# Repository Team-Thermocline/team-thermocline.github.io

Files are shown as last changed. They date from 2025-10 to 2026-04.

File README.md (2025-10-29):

# thermocline.github.io

SNHU 2025-2026 capstone project.
Team Thermocline.

# Building this website

To run this project locally using Vite, follow these steps:

Clone this repo.
```shell
git clone https://github.com/Team-Thermocline/thermocline.github.io.git
cd thermocline.github.io
```

Install deps
```shell
npm install
```

Run the dev server
```shell
npm run dev
```

# Tools

Make a new update
```shell
npm run new-update
```

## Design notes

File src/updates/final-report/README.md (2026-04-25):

---
date: 2026-04-25
---

# Final Report

Our final report

Abstract:
SNHU’s final capstone course required students to collaborate across engineering disciplines to
design, fabricate, test, analyze, optimize, and present a working product that satisfied customer
requirements. Each student brought their unique mechanical and electrical experience to help
develop the final product: a thermally-controlled PCB testing chamber that delivered efficient and
highly successful performance. Team Thermocline was originally presented with several driving
requirements provided by the customer – an electrical engineering professor, which described
product dimension, function, and performance criteria. From this, the group developed a
conceptual design, including materials, components, control features, and the expected assembly
integration process. Trade studies were then conducted across the project, supported by external
consultations with engineering, HVAC, and manufacturing/machining professionals to approve – or
improve – the product design. Initial studies included prototype electronic boards and mechanical
parts to test supply chain capabilities and electronic performance feasibility. The team built on
these initial steps by designing the mechanical structure, creating the main electronic control
board, sourcing thermal-fluid components, ordering critical pieces, and 3D-printing/laser-cutting
parts. Assembly was supplemented with iterative designing, prototyping, and functional testing of
individual subsystems. The end of the course brought performance testing to observe alignment
with customer requirements, and presenting to relevant project stakeholders. Proper
documentation was completed throughout the project, showing clear product development
history. By the end, all system and driving customer requirements were met, achieved by
persistent, insightful, and collaborative teamwork. However, one derived requirement was not met
(CON-05), describing the prohibition of thermal control when the user is handling the PCB. This
resulted from a lack of testing with physical PCBs inside the chamber, and implementing the
necessary sensors/measurements/controls to enforce this requirement. In spite of this, the team
successfully designed, built, and tested the thermally-controlled chamber that met/exceeded
most requirements, and served as an enlightening experience for developing well-rounded
engineers.

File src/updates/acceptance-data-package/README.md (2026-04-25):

---
date: 2026-04-23
---

# Acceptance Data Package

The Acceptance Data Package contains all CAD, writeup, design and software/firmware
resources for the entire project.

Its a lot to download!

|               File Name                |  Type   |                                        Description                                         |
| -------------------------------------- | ------- | ------------------------------------------------------------------------------------------ |
| ADP Summary Index                      | .docx   | *This document                                                                             |
| Bundle-3d-printing-kit                 | .zip    | All .stl/.stp files used for 3D printing prototypes and final parts                        |
| Bundle-gasket-kit                      | .zip    | CAD files for gaskets/seals                                                                |
| Bundle-scs-order-1                     | .zip    | CAD files used in purchasing SendCutSend panels (order #1)                                 |
| Bundle-scs-order-2                     | .zip    | CAD files used in purchasing SendCutSend panels (order #2)                                 |
| Bundle-scs-order-3                     | .zip    | CAD files used in purchasing SendCutSend panels (order #3)                                 |
| Bundle-scs-order-4                     | .zip    | CAD files used in purchasing SendCutSend panels (order #4)                                 |
| Controller Board BOM (LCSC)            | .xl     | Controller board materials/parts                                                           |
| Controller Board Gerbers               | .zip    | Controller board design files                                                              |
| Controller Manual                      | .pdf    | Instruction manual for product specifications, installation, and troubleshooting           |
| Developmental Steps                    | .zip    | Design plan documents and test results related to the technical development of the product |
| Team Thermocline Poster                | .pdf    | Final poster used in the open-house presentation                                           |
| thermocline_controller_v1.1-1-g5ebd8be | .uf2    | Controller firmware                                                                        |
| Thermocline Logos.zip                  | .zip    | Vector graphics, PNG graphics and original logo/style design components                    |
| ThermoclineHMI_V0.2.tar.gz             | .tar.gz | Tarball of the HMI firmware                                                                |

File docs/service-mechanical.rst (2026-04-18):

******************
Mechanical Service
******************

Regular Maintenance
===================

Serivce schedule is based on our best guess, we have not tested the machine for months at a time and certainly not a year.
Feel free to edit this page and adjust to the schedule that presents itself.

+----------------------------+-----+------+-------+-------+--------+--------+------------+
|                            | 1hr | 6hrs | 10hrs | 50hrs | 100hrs | 500hrs |  1000hrs   |
+============================+=====+======+=======+=======+========+========+============+
| Chamber gasket             |     |      |       | x     | x      | x      | x          |
+----------------------------+-----+------+-------+-------+--------+--------+------------+
| Check door gasket          |     |      |       |       | x      | x      | x          |
+----------------------------+-----+------+-------+-------+--------+--------+------------+
| Refrigerant System         |     |      |       |       |        |        | Run yearly |
+----------------------------+-----+------+-------+-------+--------+--------+------------+
| Check Internal Fan         |     |      |       | x     |        |        |            |
+----------------------------+-----+------+-------+-------+--------+--------+------------+
| Chamber Level              |     |      |       |       | x      |        |            |
+----------------------------+-----+------+-------+-------+--------+--------+------------+
| Check condenser attachment |     |      |       |       | x      |        |            |
+----------------------------+-----+------+-------+-------+--------+--------+------------+
| 3D Prints                  |     |      | x     |       |        |        |            |
+----------------------------+-----+------+-------+-------+--------+--------+------------+

See runtime hours in the **Debug Values** section of the HMI touch screen (:ref:`hmi-debug-values`).

System Structure
================

Inside the insulation houses the main chamber core. The basic assembly looks like this:

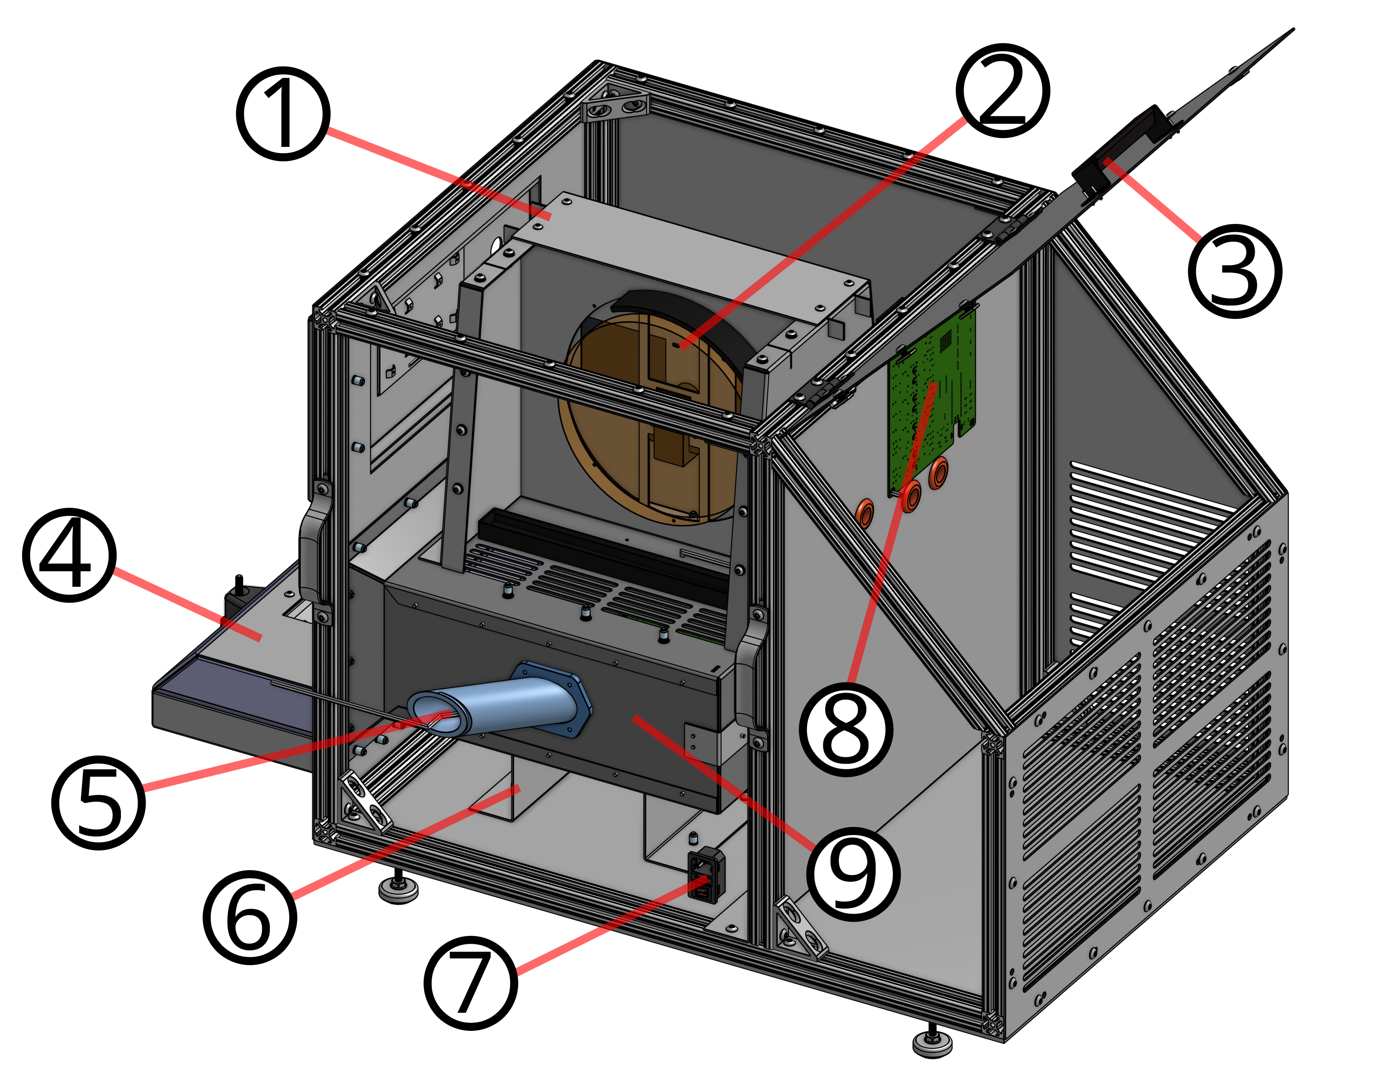
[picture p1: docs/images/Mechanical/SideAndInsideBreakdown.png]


+--------+----------------------------+
| Number |        Description         |
+========+============================+
| 1      | "Trapezoid" outer paneling |
+--------+----------------------------+
| 2      | Circulation Fan            |
+--------+----------------------------+
| 3      | Machinery Access Door      |
+--------+----------------------------+
| 4      | Chamber Door               |
+--------+----------------------------+
| 5      | Wire Passthrough Port      |
+--------+----------------------------+
| 6      | Chamber Pedestal           |
+--------+----------------------------+
| 7      | IEC Receptacle             |
+--------+----------------------------+
| 8      | Chamber Controller Board   |
+--------+----------------------------+
| 9      | Chamber Shroud             |
+--------+----------------------------+

Installing and Uninstalling panels
==================================

The chamber is built with many laser cut panels. These panels are held to an internal aluminum
extrusion frame with 1/4-20 screws and nuts, as well as 10-32 screws and rivnuts in some places.

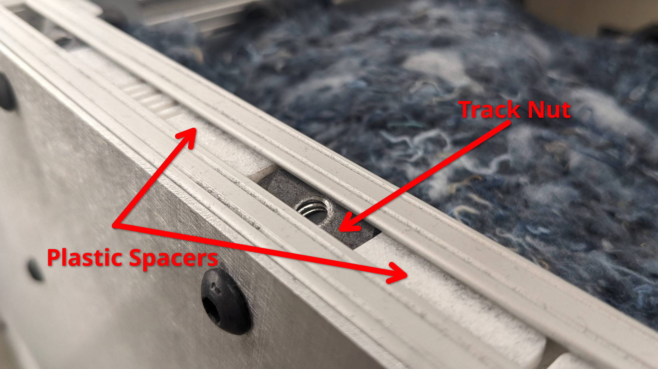
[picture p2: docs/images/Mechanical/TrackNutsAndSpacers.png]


.. note:: When installing screws, the track nuts can often become missaligned. Leave all screws loose until each screw is started, then tighten down. This allows some flexibility to correct missalignment.

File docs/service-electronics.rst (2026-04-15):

******************
Electrical Service
******************

Main Board
==========

The Main Board is the central controller PCB for the thermal testing chamber. It handles all the critical measuremnts, the high-power switching
and the centeral interconnect between HMI, a user laptop and the physical hardware.

Schematics
==========

The schematic files are stored on our 
`GitHub repository <https://github.com/Team-Thermocline/Controller/tree/main/Hardware/Main-Board>`_, 
but can also be viewed via `KiCanvas <https://kicanvas.org/>`_ 
on the web or at the end of the printed PDF Manual.

+-------------+---------------------------------------------------------------------------------------------------------------------------------------------------------------------------------------------------------------+
| Full System | `Full System Schematic <https://kicanvas.org/?repo=https%3A%2F%2Fgithub.com%2FTeam-Thermocline%2FController%2Fblob%2Ffeat%2Ffull_system_schematic%2FHardware%2FComplete-System%2FComplete-System.kicad_sch>`_ |
+=============+===============================================================================================================================================================================================================+
| Mainboard   | `Mainboard Interactive Schematic <https://team-thermocline.github.io/schematics/Main-Board.html#/>`_                                                                                                          |
+-------------+---------------------------------------------------------------------------------------------------------------------------------------------------------------------------------------------------------------+

Fuses
=====

The chamber uses 6 fuses total. One on the IEC plug on the side. And five more on the main board under
the rear panel.

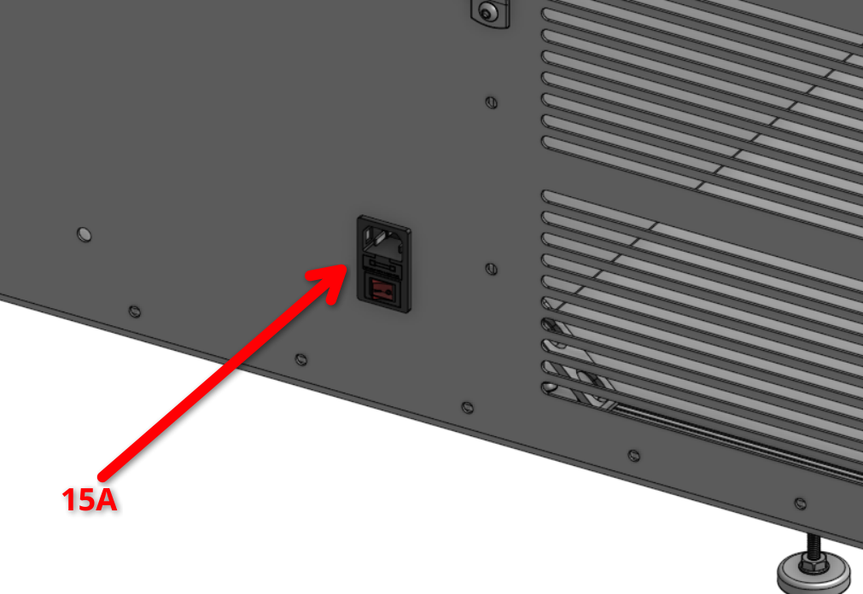
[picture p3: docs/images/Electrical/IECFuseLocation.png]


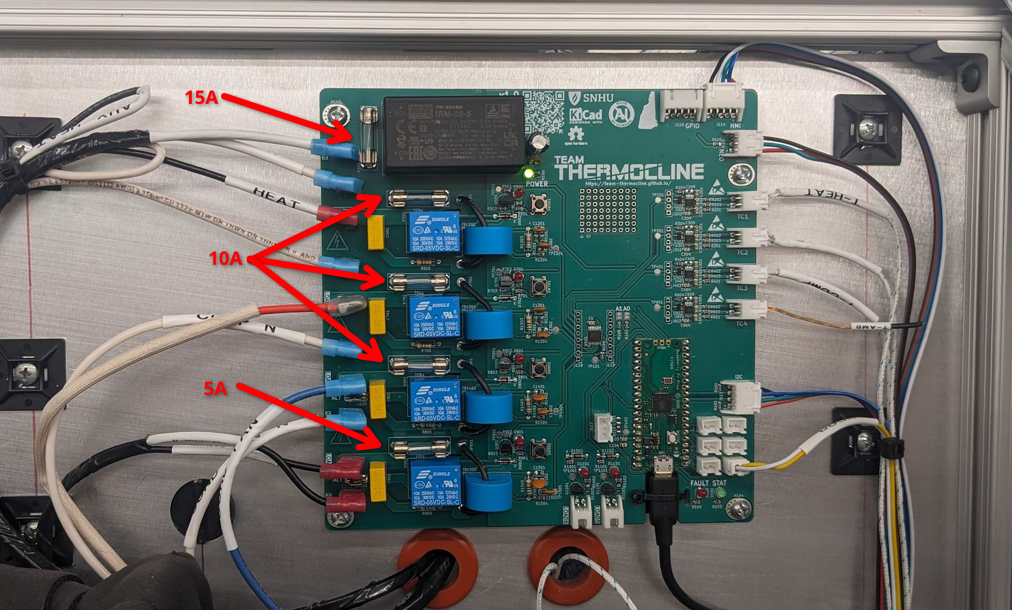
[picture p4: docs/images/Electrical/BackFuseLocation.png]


There are three main fuses sizes, 15A, 10A and 5A.

.. warning:: Power the system down and unplug it before changing fuses! Fuses are LIVE when powered on!

Decorational Panel
==================

The decorational panel is a large sheet metal panel at the front of the machine that houses the raspberry
pi 5 HMI as well as the machine USB-C port and the E-Stop button.

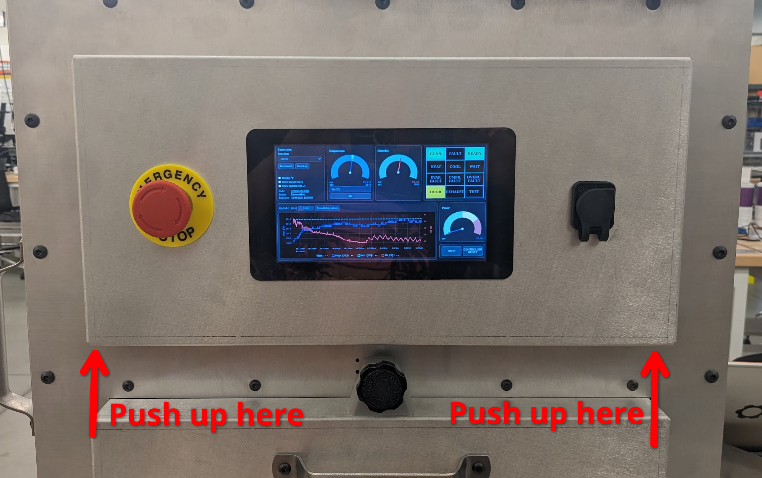
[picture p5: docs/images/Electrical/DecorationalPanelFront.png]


The panel can be removed by pushing up evenly from the bottom and pulling gently off the front. It is
held in place by four screws in locking slots.

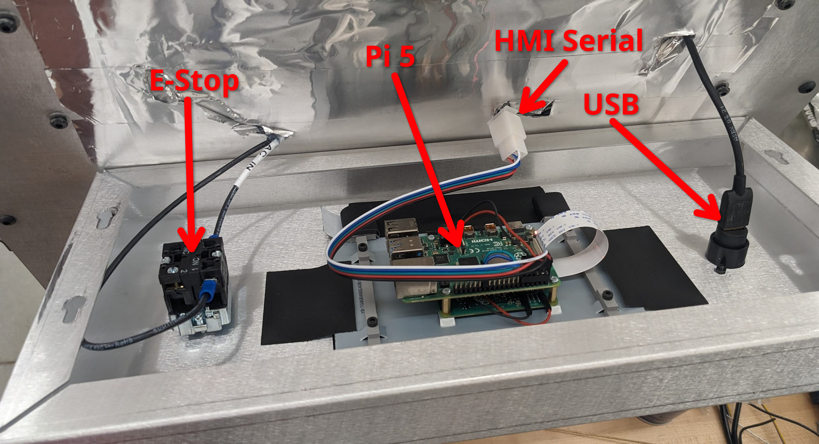
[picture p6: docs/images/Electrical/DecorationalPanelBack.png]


PCB Files
=========

* `Click here to View Layout <https://kicanvas.org/?repo=https://github.com/Team-Thermocline/Controller/blob/v1.0/Hardware/Main-Board/Main-Board.kicad_pcb>`_
  (PCB rendered and hosted on KiCanvas! There may be visual bugs; for best browsing experience view the PCB directly in KiCad!)

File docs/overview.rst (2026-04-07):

Project Overview
================

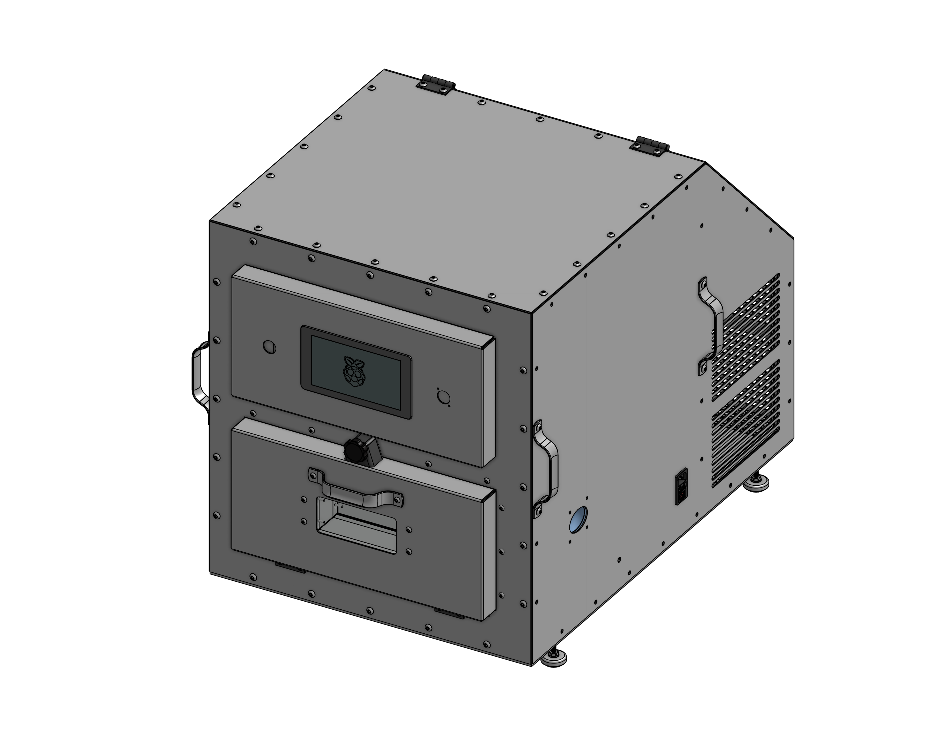
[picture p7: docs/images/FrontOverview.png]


The Team Thermocline Thermal Testing Chamber (Refered to as "The Chamber") is a thermal testing chamber designed to test the 
performance of electronic components in a controlled environment. It was designed as a 2025-2026 engineering capstone project 
at Southern New Hampshire University (SNHU).

The Chamber is 22" by 31" and weighs about 90lb. When lifting the chamber, please use at least a *two person lift*.

Powering the Chamber on
-----------------------

The chamber is powered by an IEC cable connected to a recepticale on the right side of the machine (when facing the front).
Please note the chamber is fused for 15A.

There are two AC interlocks, one is the red switch on the side controlling the system power, the other is the E-Stop button on
the front. Both must be in the "on" position for the chamber to power on. Twist the E-Stop button to reset it back to on.

The chamber uses both a raspberry pi pico as the primary controller and a raspberry pi 5 as a build-in screen. The pico
should boot almost imedietly after power is applied, and should turn on the chamber lights.
*The pi 5 may take one or two minutes to boot.*

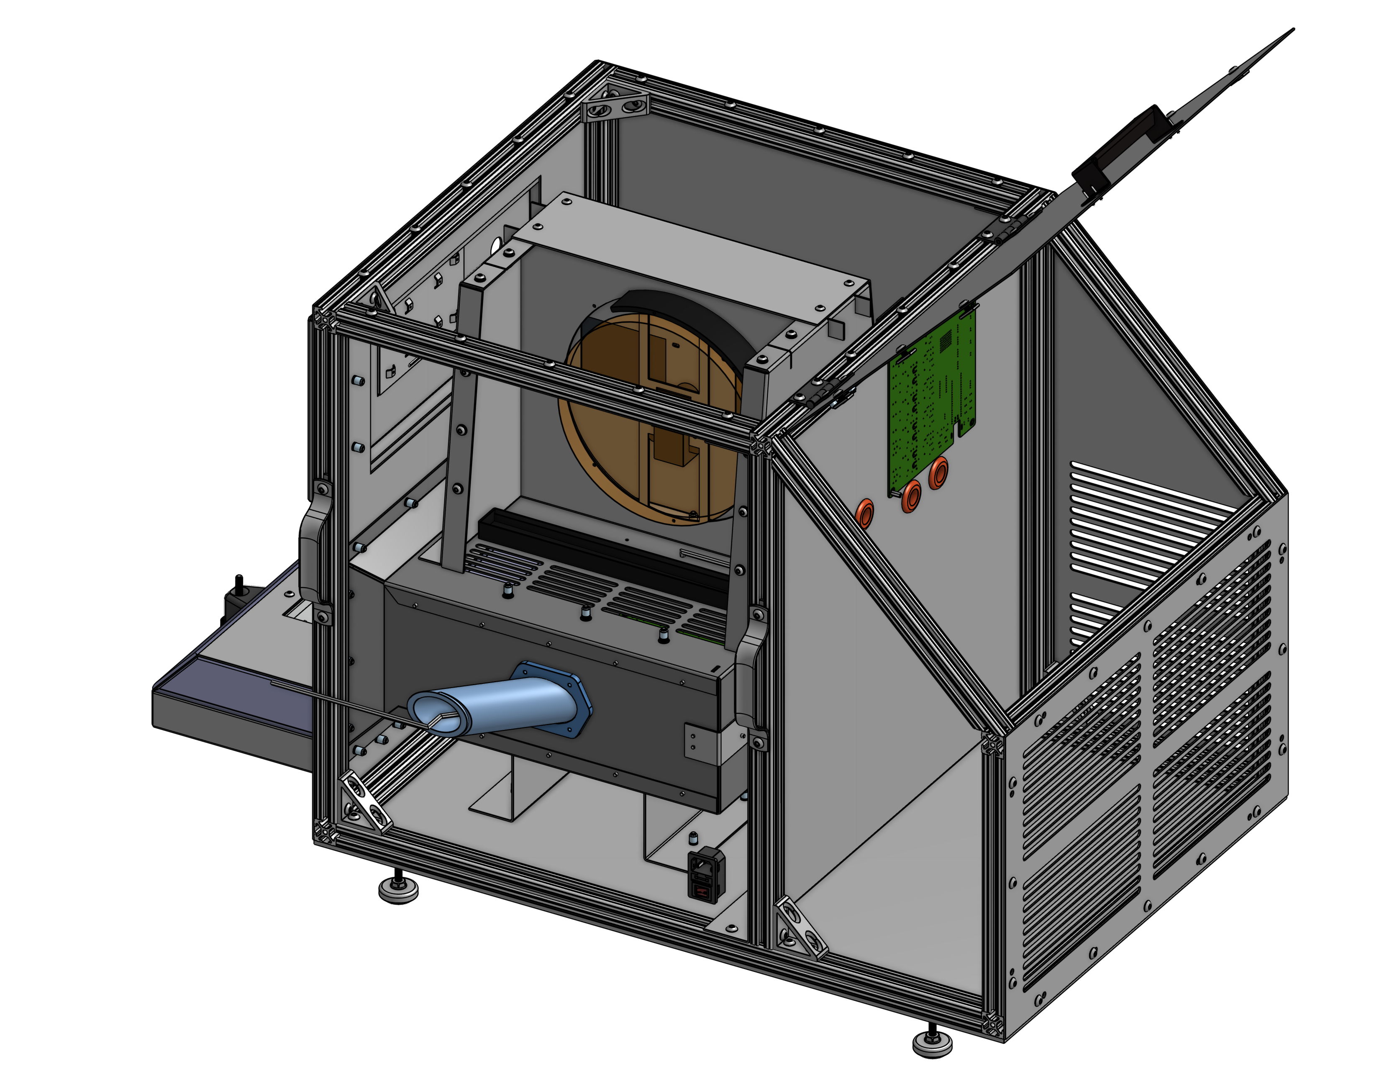
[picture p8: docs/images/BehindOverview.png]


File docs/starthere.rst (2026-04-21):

**********
Start Here
**********

The Team Thermocline Thermal Testing Chamber (Refered to as "The Chamber") is a thermal testing chamber designed to test the 
performance of electronic components in a controlled environment. It was designed as a 2025-2026 engineering capstone project 
at Southern New Hampshire University (SNHU).

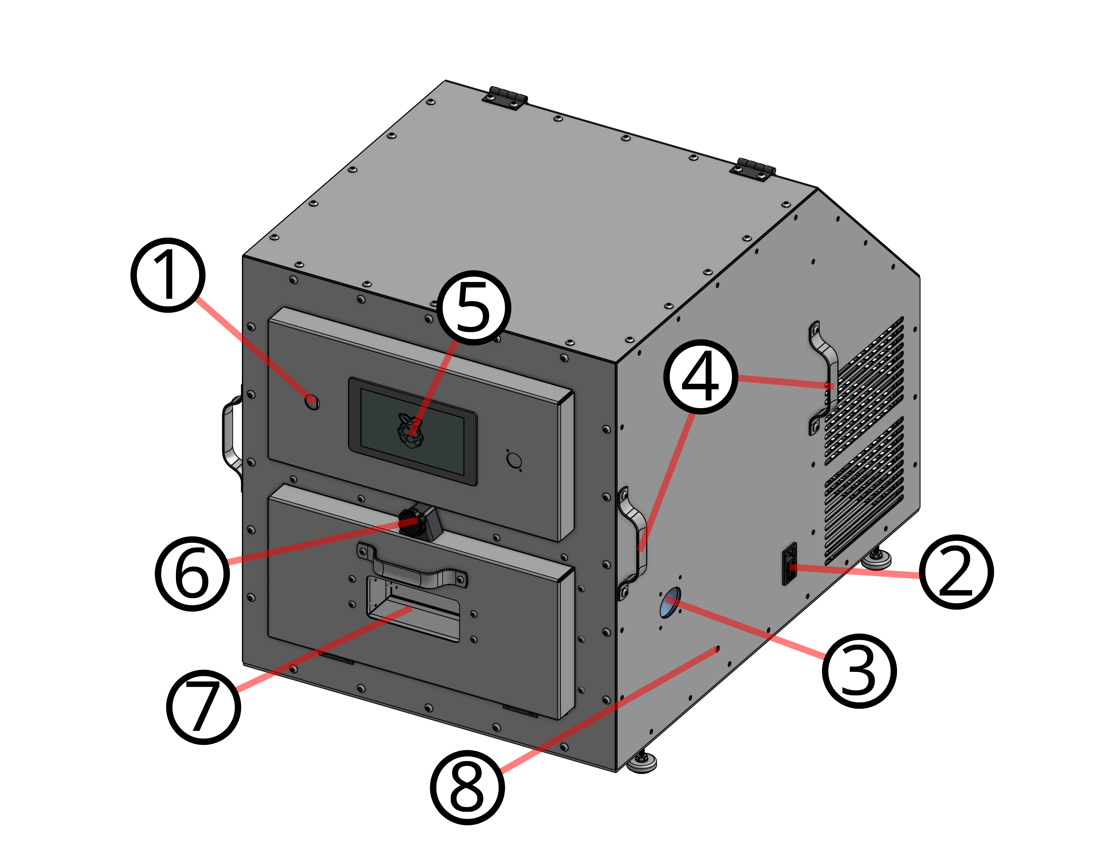
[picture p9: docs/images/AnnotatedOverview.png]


+--------+-----------------------+
| Number |      Description      |
+========+=======================+
| 1      | E-Stop Button         |
+--------+-----------------------+
| 2      | IEC Receptacle        |
+--------+-----------------------+
| 3      | Wire Passthrough Port |
+--------+-----------------------+
| 4      | Lifting Handles       |
+--------+-----------------------+
| 5      | HMI Touch Screen      |
+--------+-----------------------+
| 6      | Door Locking Clamp    |
+--------+-----------------------+
| 7      | Viewing Window        |
+--------+-----------------------+
| 8      | Condensate Drain Port |
+--------+-----------------------+

This manual references things in terms of **Left** and **Right** side of the machine.

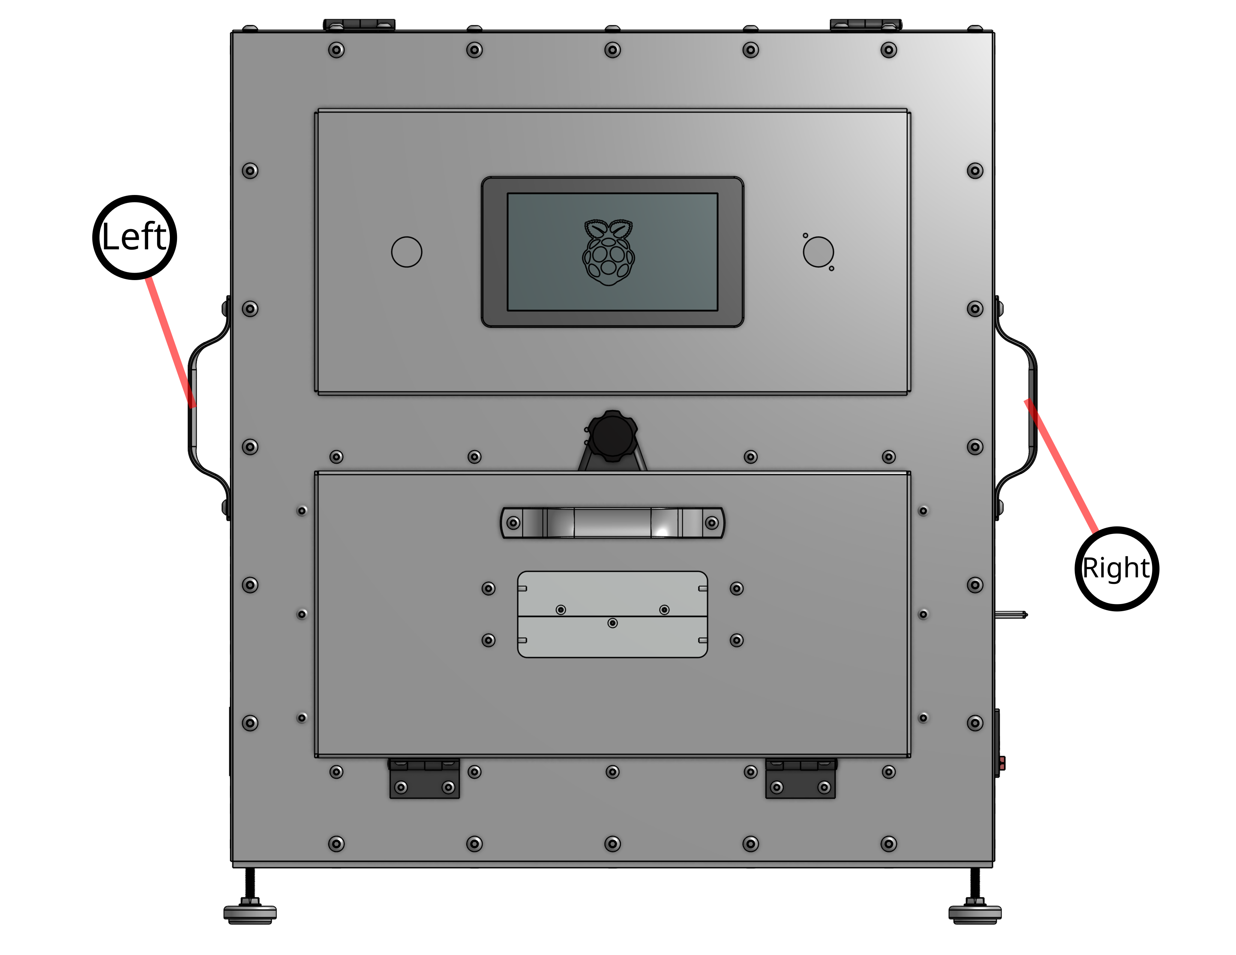
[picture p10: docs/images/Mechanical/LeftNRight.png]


Moving the Chamber
==================

.. warning:: The Chamber is 22" by 31" and weighs about 125lb. When lifting the chamber, please use at least a *two person lift*.

The chamber has handles located on either side. With two or four people, lift each handle vertically 
to move the chamber. Do not rotate the chamber as this may cause fluids to move into unintended parts
of the plumbing. Do not shake or jostle the chamber as hard shocks can damage plumbing.

.. note:: Because the cooling system of the chamber can collect water, the chamber should be leveled
    along its long axis to allow for proper drainage.

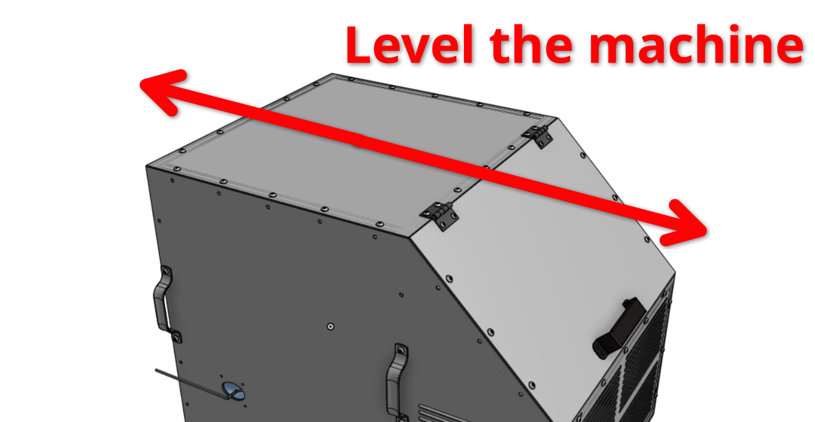
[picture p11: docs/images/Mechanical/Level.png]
    

Place the chamber in such a way that there is enough area to vent air directly out the back.
Allow for no less than **8"** of clearance behind the chamber.

Powering the Chamber on
=======================

The chamber is powered by an IEC cable connected to a recepticale on the right side of the machine (when facing the front).

There are two AC interlocks, one is the red switch on the side within the IEC receptacle(2), the other is the E-Stop button on
the front(1). Both must be in the "on" position for the chamber to power on. Twist the E-Stop button to reset it back to on.

The chamber uses both a raspberry pi pico as the primary controller and a raspberry pi 5(5) as a build-in screen. The pico
should boot almost imedietly after power is applied, and should turn on the chamber lights.
**The pi 5 may take one or two minutes to boot.**

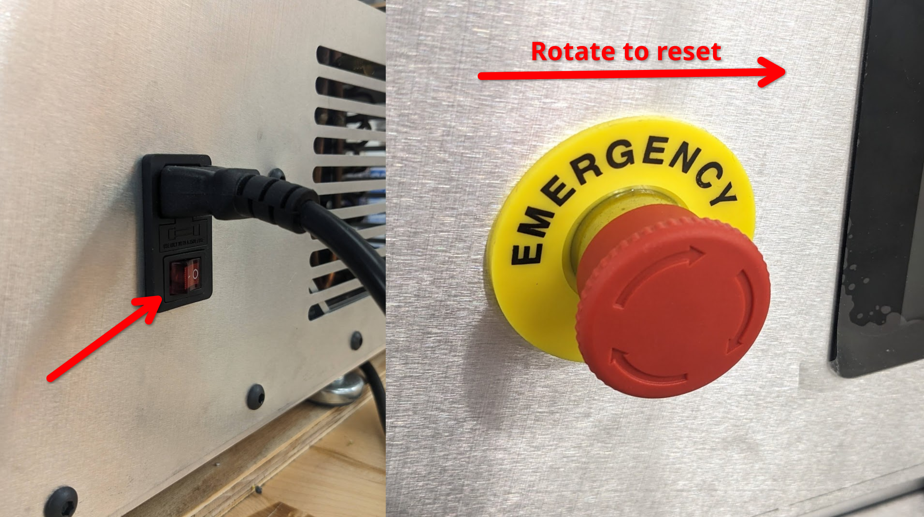
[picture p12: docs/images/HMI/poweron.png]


Using the HMI Touch Screen
==========================

Once the HMI is booted (which can take one to two minutes), you should see the main HMI screen.

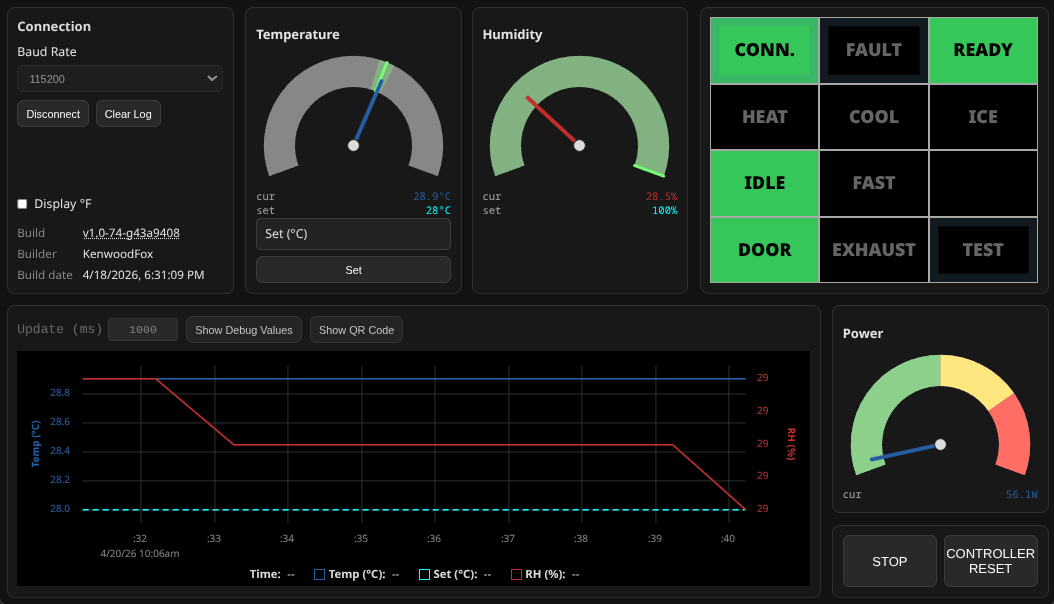
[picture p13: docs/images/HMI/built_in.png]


In the top right are the status indicators, they may change color or flash to indicate important information.

+-------------+---------------------------------------------------------------------------------------+
|  Indicator  |                                         Desc.                                         |
+=============+=======================================================================================+
| CONN.       | Shows connection to the controller board.                                             |
+-------------+---------------------------------------------------------------------------------------+
| FAULT       | Indicates a current fault.                                                            |
+-------------+---------------------------------------------------------------------------------------+
| READY       | Green when ready to run or running, flashing green when you've reached your setpoint. |
+-------------+---------------------------------------------------------------------------------------+
| HEAT        | Indicates the heater is on.                                                           |
+-------------+---------------------------------------------------------------------------------------+
| COOL        | Indicates the cooler is on.                                                           |
+-------------+---------------------------------------------------------------------------------------+
| ICE         | Flashes yellow for suspected ice; flashes green during DEHUMIDIFY.                    |
+-------------+---------------------------------------------------------------------------------------+
| IDLE        | Solid green when MACHINE is IDLE                                                      |
+-------------+---------------------------------------------------------------------------------------+
| CMPR. FAULT | Indicates a fault in the compressor.                                                  |
+-------------+---------------------------------------------------------------------------------------+
| FAST        | Flashes yellow when controller is ramping as fast as it can                           |
+-------------+---------------------------------------------------------------------------------------+
| DOOR        | Indicates the door is open or not properly tightened down.                            |
+-------------+---------------------------------------------------------------------------------------+
| EXHAUST     | Indicates the condenser fan is being held on for cooling the machinery space.         |
+-------------+---------------------------------------------------------------------------------------+
| TEST        | Indicates the chamber is in test mode.                                                |
+-------------+---------------------------------------------------------------------------------------+

On the left you may choose to display temperature readings in Fahrenheit or Celsius.
You may also choose to log or not log keepalive messages as well as Q0 updates though without
a laptop connected these messages will not be shown either way.

You may choose the amount of time between Q0 updates, the default is 1000ms (1 second).

The buttons on the bottom right will set the mode of the chamber to STANDBY upon pressing the STOP button,
or reset the controller upon pressing the CONTROLLER RESET button.

.. warning:: Resetting the controller will cause it to loose its sense of time. If the controller does not know when it last ran the compressor, it may try to run the compressor too early and this could cause an overcurrent fault.

Using the Website Sender
========================

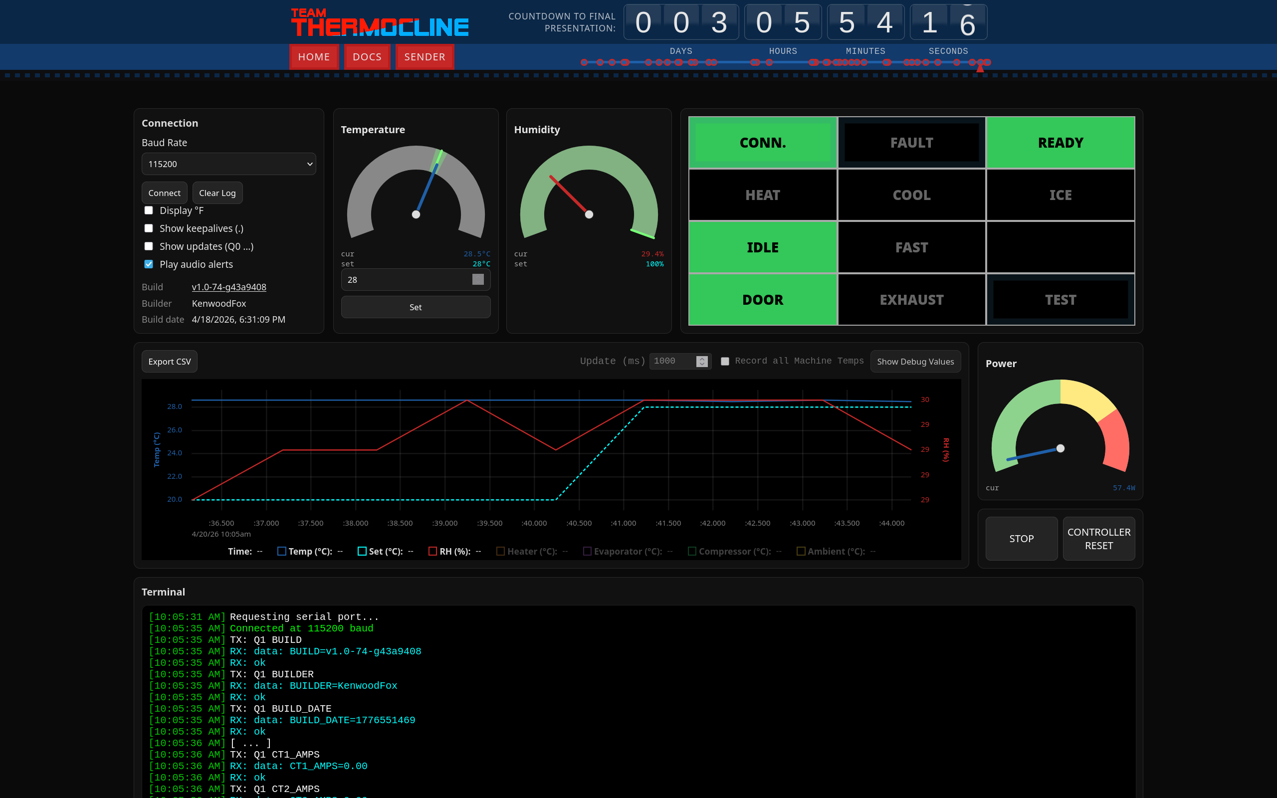
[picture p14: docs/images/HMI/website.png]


For better controls, enhanced monitoring and data export, you may connect the chamber
to a personal laptop using the USB-C port on the front of the machine. Navigate to https://team-thermocline.github.io/#sender or scan the QR code below.



The website view has all the same information as the HMI touch screen with the addition of some
features such as being able to log all the temperature readings at once to the graph and exporting
the data as a .csv file.

.. _hmi-debug-values:

Debug Values
============

On both the Website and the HMI touch screen, you may press the "Show Debug Values" button to see
more sensor information provided by the controller board, these can include
the temperature of the heater, evaporator, compressor, and ambient temperature.
Current CPU load, discovered I2C devices, safety timing lockouts as well as build and historical
information.

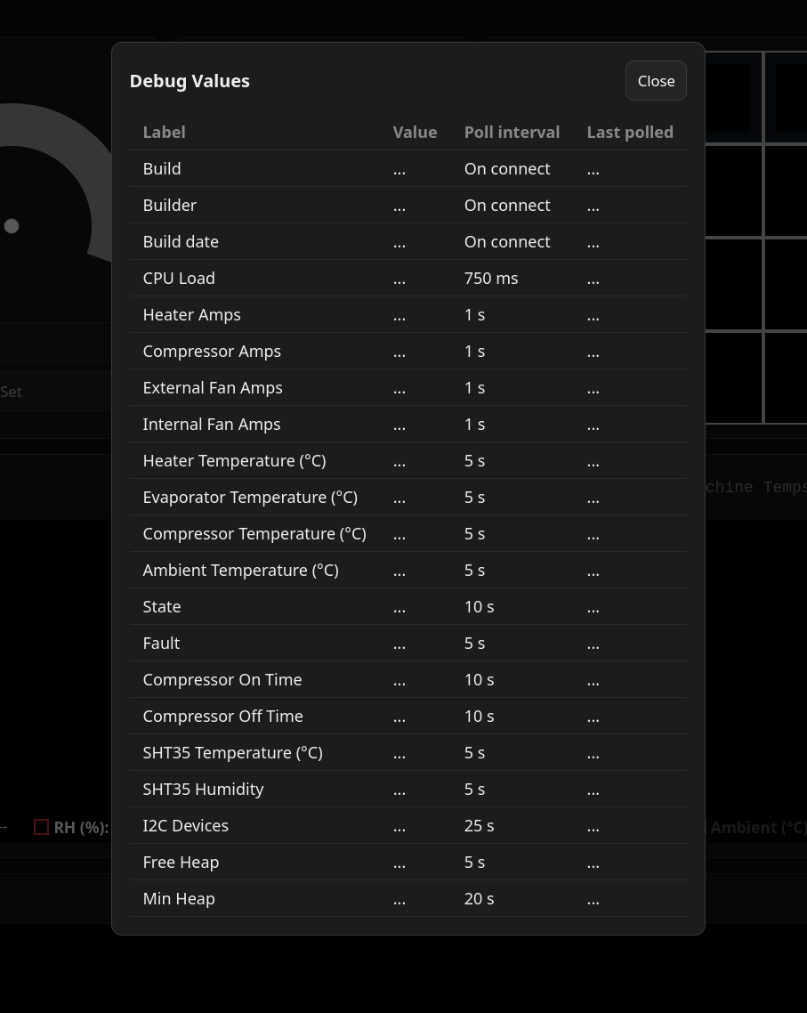
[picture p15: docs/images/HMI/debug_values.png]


Debug values are color coded to what the website expects "standard values" should be. These may not
always corrolate with normal or preciesly expected values, but are meant to be a simple
troubleshooting aid to guide your eye toward anything clearly wrong.

Troubleshooting
===============

The controller is programmed to protect its most sensitive refrigerant components as well as human safety.
To this end, it will shut down and enter fault or standby mode any time it detects a fault.
Faults come with unique ASCII readable error codes. This table does not include
all possible faults but the most common and their imediete mitigations.

.. list-table:: Common fault codes
   :header-rows: 1
   :widths: 40 60
   :class: longtable

   * - Error code
     - Description
   * - | ``COMMUNICATION_ERROR``
       | ``FAULT_CODE_I2C``
     - One of the i2C devices on or off the board is not responding. Check debug values, the ADG chip is the only i2C device on board. If the SHT35 does not show up, check the i2C connector on the lower right hand of the board.
   * - | ``OPEN``
       | ``FAULT_CODE_THERMOCOUPLE``
     - Any thermocouple becoming disconnected is cause for a FAULT since the controller relies on their values to run many important control loops. Inspect the TDR0-3 input JST plugs on the upper right of the control board.
   * - | ``OVERCURRENT``
       | ``FAULT_CODE_COMPRESSOR``
     - The compressor went overcurrent on startup or during operation. Wait at least **ten minutes** before restarting the compressor after an overcurrent fault. The motor may have stalled.
   * - ``FAULT_CODE_ENV_SENSOR``
     - The internal SHT35 or another internal sensor faulted while running. Check the i2c connection and the sensor itself.
   * - ``FAULT_CODE_OVERCURRENT``
     - Any load went overcurrent during operation. Check fans and heaters. Use the debug values to monitor current when running.

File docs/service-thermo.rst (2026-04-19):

*********************
Refrigeration Service
*********************

.. warning:: The refrigeration system is complex and potentially dangerous. It should only be serviced by those 
    qualified and **licensed**. We performed all assembly under the supervision and experience of licensed 
    professionals. And we hope future maintainers of the machine will do the same.

System Structure
================

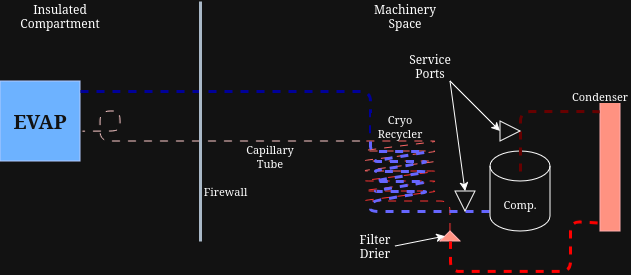
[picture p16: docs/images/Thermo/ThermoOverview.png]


The refrigeration system is a closed loop system that uses R410 refrigerant to cool the chamber.

The system is composed of the following components:

- Compressor
- Condenser
- Recycler
- Evaporator
- Capillary Tube

Most of the machinery lives in the machinery space at the back of the chamber, accessed by the hinge machinery door.

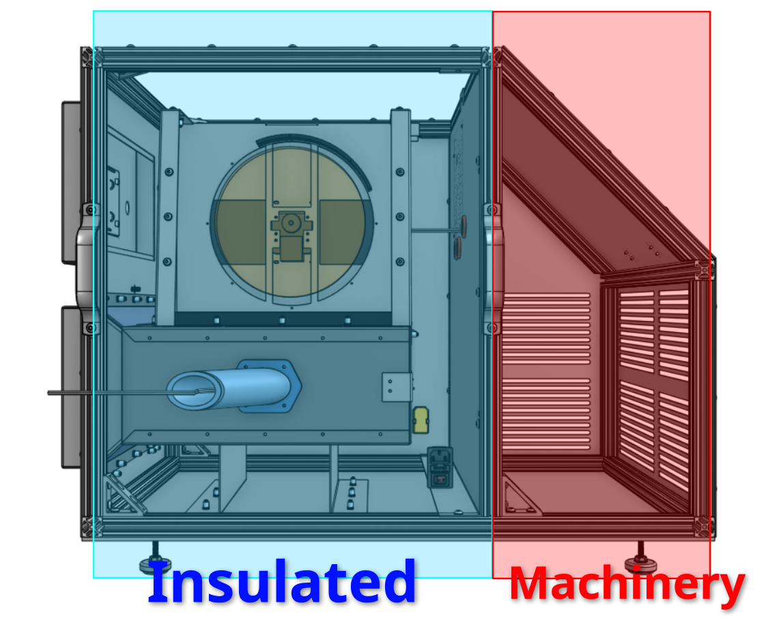
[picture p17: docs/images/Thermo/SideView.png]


We purposefully installed two service fittings on the machine, one on the cold low pressure return side and one on the
high pressure hot side.

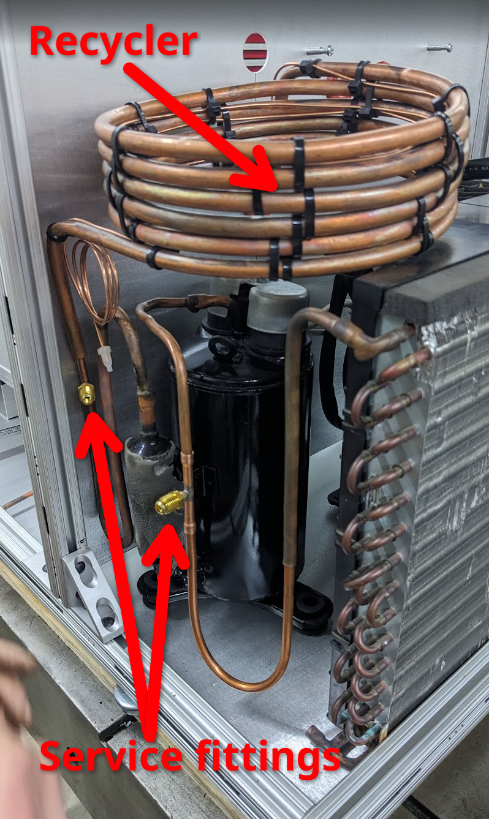
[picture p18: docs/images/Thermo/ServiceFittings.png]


We initally charged the system with around **1lb** of R410. This seemed like enough under inital testing to keep the
condensor with a good reserve at all times.
The condensor is many times larger than the evaporator or the flow that can be sustained through the capillary tube.

Specifications and Service Notes
================================

+-------------------------+--------+
|      Specification      | Value  |
+=========================+========+
| Refrigerant             | R410   |
+-------------------------+--------+
| Compressor              | 1/2 HP |
+-------------------------+--------+
| Capillary Tube Length   | 10ft   |
+-------------------------+--------+
| Capilalry Tube Diameter | 0.7mm  |
+-------------------------+--------+
| Total System Volume     | 2160cc |
+-------------------------+--------+
| Refrigerant Charge      | 1lb    |
+-------------------------+--------+

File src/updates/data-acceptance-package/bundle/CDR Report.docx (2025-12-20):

CDR Report

Authors:

Nikolai DiLullo, Alexandra Friebolin, Alexia Hnatowicz, Jacob Morrissette, Joe Sedutto

Professor McInnis and Professor Guo
EG498 Capstone Design I
Fall 2025

# Table of Contents

# List of Tables

Table 2.1: Structural Requirements

Table 2.2: 5052 H32 0.063” Aluminum Material Properties (Send-Cut- Send)

Table 2.3: Insulation Trade Studies

Table 2.4: Current Best Estimate for Structural Weight

Table 3.1: Thermo-Fluid Requirements

Table 3.2: Cooling Trade Studies

Table 4.1: Internal Safety Requirements

Table 4.2: External Safety & User-Contact Requirements

Table 4.3: Operation & Fault-Response Requirements

Table 4.4: Safe-State Requirements

Table 5.1: Electrical Components Requirements

Table 5.2: Heating Trade Study

Table 6.1: Customer/System Requirements

Table 6.2: Control System Requirements (Part A)

Table 6.3: Control System Requirements (Part B)

Table 6.4: Screen Selection Trade Study

Table 6.5: MCU Trade Study (Part A)

Table 6.6: MCU Trade Study (Part B)

Table 8.1: Verification Matrix

Table 11.1: Itemized Purchased Budget

Table 11.2: Overall Budget

# List of Figures

Figure 2.1: Aluminum Handle Prototype

Figure 2.2: Chamber External Assembly

Figure 2.3: Frame Assembly Views

Figure 2.4: 8 Panel Design

Figure 2.5: PCB Testing Chamber & Support

Figure 2.6: Airflow Management Compartment

Figure 2.7: HMI Display Mount

Figure 2.8: Chamber Door Handle Design

Figure 4.1: Current Transformer

Figure 5.1: Electrical Flowchart

Figure 5.2: Interconnect board

Figure 5.3: Current PCB Layout

Figure 6.1: CrowPanel 7.0 ESP32

Figure 6.2: Thermocline GUI Prototype, LVGL block

Figure 6.3: Thermocline State Machine

Figure 6.4: Overview of Task State Management

Figure 6.5: Example JSON Packet

Figure 6.6: Example of electrical arcing across relay contacts Source: Wikipedia

Figure 7.1: Risk Tables

Figure 7.2: Risk Matrix

# Project Description

### Customer Requirements

The customer requires the development of a controlled temperature chamber for evaluating the performance of electronic components under varying thermal conditions. The chamber must accommodate a 12″×12″ printed circuit board and incorporate a sealed port for routing external electrical connections needed for stimulus and measurement. It must be constructed with appropriate insulation to minimize thermal losses and equipped with the ability to heat and cool the internal volume across the commercial operating range of 0°C to 70°C while maintaining the temperature within ±3°C of the setpoint. In addition, the system must include internal temperature monitoring and provide recorded data. These capabilities are necessary to support reliable and repeatable component testing as specified by the project sponsor, Dr. Monk.

### Solution Description

The solution will be in the form of a labratory appliance. It will be installed on a table no deeper than 30” to accommodate labratory table depth. It will be no wider than 30” to take up excess space. The system will run indoors, use standard AC wall power (120V, 60HZ). Will not require external ducting or pumbing. And will not require (but may optionally include) external, remote or computer control.

### ConOps Summary

The Concept of Operations (ConOps) outlines the intended function, environment, and operational behavior of the thermally controlled PCB testing chamber. The system is a tabletop, insulated chamber designed to accommodate 12″×12″ PCBs and regulate internal temperature within the commercial range of 0–70°C while maintaining ±3°C accuracy. It operates in an indoor laboratory environment with stable power, proper ventilation, and access to PC-based data logging. The chamber supports multiple operating modes—including Shutdown, Standby, Start, and Safe states—and allows users to insert test boards, connect measurement cables, and monitor temperature performance locally or remotely. The ConOps identifies primary stakeholders such as engineers, maintenance personnel, faculty, and material suppliers, all of whom contribute to system design, operation, and lifecycle support. It also evaluates operational impacts, including thermal hazards, electrical safety concerns, ventilation requirements, spatial constraints, and data management needs. Finally, the ConOps provides a structured risk assessment addressing potential failures in design, fabrication, operation, and maintenance, assigning likelihood and consequence values to prioritize mitigation efforts. Collectively, the ConOps establishes a clear operational framework that informs system requirements, guides engineering decisions, and ensures safe, reliable, and traceable thermal testing of electronic components.

# Subsystem: Structural - Mechanical

### System Requirements

The structural subsystem requirements are strict guidelines for the final system that must be adhered to for a successful project. The product must satisfy both customer and team design specifications – arising from design considerations, project timelines, available resources, financial budgets, or product needs. The following database in Table 2.1 represents the team’s structural subsystem requirements as of the Preliminary Design Review, which specifics are subject to change later depending on customer modifications, team discussions, or design updates from testing.

Number | Requirement | Performance | Margin | Verification
STR-01 | The system shall have external base dimensions of no more than 30x30 inches. | 30x30 in | -2x2 in | Inspection
STR-02 | The system shall have internal base dimensions of no less than 12x12 inches. | 12x12 in | +2x2 in | Inspection
STR-03 | The chamber opening(s) shall include proper thermal sealing according to ASTM F1886 | Complies | N/A | Inspection
STR-04 | The internal thermal control components shall include proper thermal sealing according to ASTM C633-01. | Complies | N/A | Inspection

Table 2.1 Structural Requirements

The following notes provide further detail on each requirement:

STR-01 is a customer-provided requirement. Considering the product’s end-usage will be a local operating table-top system, it should be able to fit conveniently on most SNHU tables, desks, and benches without protruding from their edge; having a requirement that limits the external base dimensions of the system will satisfy the customer’s desire to have an easily accessible, movable, and safe system. The margin of -2x2 inches, although relatively small, can be modified with both a customer- and team-agreement since the lower bound is more flexible, as it constricts dimensions below 30x30 inches. Although smaller dimensions will constrict internal area and component-arrangements, this design decision will most likely save costs, material, and fabrication time. The final system’s external base dimensions shall be measured and inspected to verify if the requirement is met.

STR-02 is also a customer-provided requirement. In order for the final product to evaluate PCB performance, it must first adequately fit the PCB without mechanical/electrical damage or complicated installation. Thus, the system should incorporate an internal floor space of at least 12x12 inches. Tighter areas could satisfy smaller PCBs, but would fail at incorporating the largest. Designing an area larger than this provides room for possible extruding components from the PCB, as the “tester” dimensional specifications are contemporarily unknown at the time of this design report. The margin for this requirement of +2x2 inches is stricter than STR-01—where the team aims closer to the performance value, as larger than 12x12 inches could reduce insulation and prompt larger external dimensions.

STR-03 is a team-determined requirement, derived from Design Requirement 1.2: Included Insulation. Since the system will have external wiring for its power supply and connections to the tested-PCB, structural openings are inevitable. These ports must thus be properly sealed in order to still satisfy being insulated and safe. ASTM F1886 outlines a visual inspection test procedure for seal integrity to ensure the system complies (1).

STR-04 is also a team-determined requirement derived from several of the system’s safety design requirements. The internal components are concerning the thermal-fluid cooling system, resistive heating process, electronic controls, and other mechanical elements. ASTM C633-01 is a “Standard Test Method for Adhesion or Cohesion Strength of Thermal Spray Coatings”, which can be used to determine if the requirement is met (2).

### System Design

#### Trade Studies

The system design and subsystem design requirements are holistic enough to outline important dimensional, functional, operational, manufacturing process, budget, and resource constraint details. However, these regard not the system in its entirety nor account for every project detail. Therefore, numerous trade studies are carried out with the team and stakeholders—if applicable— to further progress design specifications. These trade studies can be simple through small verbal discussions, or highly detailed spanning weeks of research, testing, and analysis to provide insights into the design. The trade study determining the primary material for the system’s external framework, internal support, and housing compartments was completed through a team discussion. This study was finalized early in the design process as the team understood its implications would drive several other design considerations such as insulation, fixture attachments and joint connections, and the arrangement of other components and subsystems. Ultimately, using a 0.063” 5052 H32 Aluminum-based alloy would provide the greatest success for the final product. Its critical material property specifications are outlined in Table 2.2 below (3).

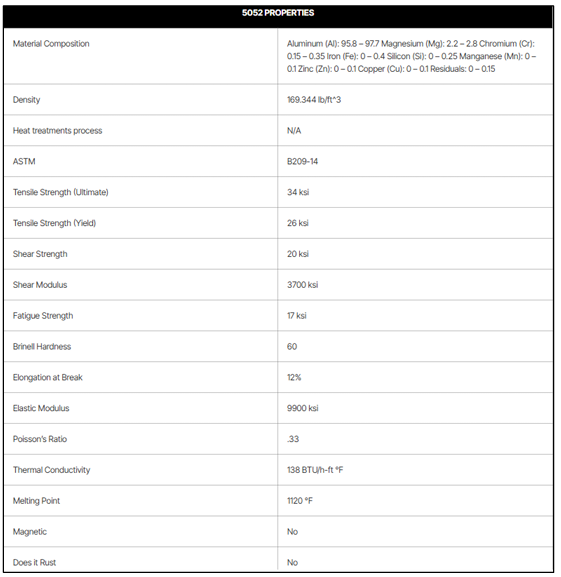
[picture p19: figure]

Table 2.2: 5052 H32 0.063" Aluminum Material Properties (Send-Cut-Send)

Through numerous discussions, this Aluminum alloy beat several other material candidates such as Carbon-Steel, Titanium alloys, glass composites, and heavy-duty plastics. The team found its general low-costs – in manufacturability, installation and repairability – to work within the given budget constraints. Its lightweight property promotes greater usability during operation and maintenance procedures, while contributing less to mechanical stress/strain for load-bearing structures. The Aluminum would also be able to withstand the mechanical and thermal conditions within the system, making it suitable for the system’s designated environmental condition range. Most prominently, Send-Cut-Send is a well-reputable manufacturer, able to fabricate the designed pieces, provide consistent and strong customer support, hold efficient lead times, perform solid quality inspections, and provide precise and highly reliable parts. Outsourcing these pieces pre-cut and bent is more feasible and cost-efficient than performing these operations in-house with parts sourced elsewhere. Moreover, for the structural subsystem, the only heavily analyzed trade study was in regard to the use of insulation material. This comparisons between several known candidates are outlined in Table 2.3.

| Fiberglass | Polyurethane Foam | Polystyrene | Silica Aerogel
Thermal Conductivity (W/(m⋅K)) | 0.032-0.036 | 0.02-0.03 | 0.025-0.04 | 0.0032-0.015
Nominal Thickness (in) | 6-12 | 1.18 | 3 | 0.2-0.4
Malleability | Most malleable | Malleable depending on type | Malleable when molten | Not malleable
Cost | $1.00-4.50/ ft^2 | $0.50-4.50 ft^2 | $1.00-4.50 ft^2 | $10,000 ft^3

Table 2.3: Insulation Trade Studies

These categories shown on the left-hand side of the table were chosen due to being ranked as highly impactful to the success of the insulation itself along with the final product. In conducting a thorough analysis, fiberglass insulation was seen as superior and would contribute to the greatest success for the overall system. Although out of the most accessible and well-known types of insulation studied it had one of the highest thermal conductivities, this value was sufficient enough to properly insulate the system/components – where the other categories increased its worth. Having a large nominal size would fit well for the system the team is designing given the large amounts of empty volume needed to be filled with insulation; this process would be simpler with how fiberglass insulation is manufactured and installed. Similarly, its higher malleability over the other candidates would simplify the installation, maintenance, or “plugging” processes, especially in smaller ports and non-uniform spaces. Lastly, being widely available and simpler to manufacture decreases its cost, reducing possible financial burdens on the team and opening room for other purchases throughout the project. Strategically weighing these four categories convinced the team to use fiberglass insulation for producing a highly effective thermally-sealing structure to the system.

Proof of Concept / Feasibility Testing

Early in the team’s research phase, the system’s structure was identified as a crucial aspect to not only the final project’s success, but an important step in conducting trade studies, developing design models, building prototypes, and optimizing subsystems. Therefore, it was important to analyze the structural subsystem and determine an appropriate constituent with significant risk or room for improvement. Since creating numerous panels and other supporting pieces with laser-cut sheet metal was under heavy consideration, the team decided to test the supply chain capability of Send-Cut-Send – given this manufacturer’s higher precision, efficiency, and ease-of-design/fabrication. By designing a simple piece – yet one that would test many of their capabilities, the team could determine whether this manufacturer was feasible down the line of the project. For this test, the chamber door handle was designed with 3D-modeling software, ordered through Send-Cut-Send, fabricated, and shipped; the design is shown in Figure 2.1. The team not only evaluated the effectiveness and efficiency of logistics for sourcing one of the primary fabrication-materials – analyzing lead time, price, company/product information – but also received profitable feedback in optimizing future metal sheet designs. This test ultimately proved the feasibility of the manufacturer and convinced the team of which materials and parts should be incorporated into the final product.

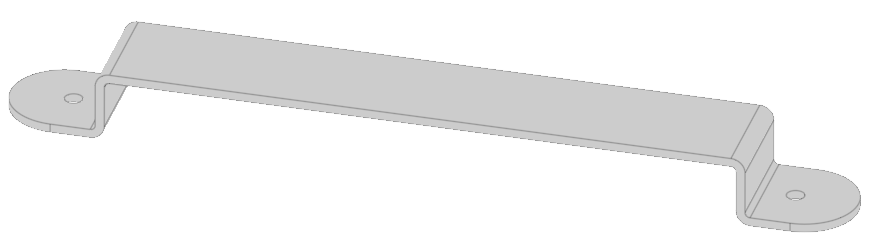
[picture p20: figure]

Figure 2.1: Aluminum Handle Prototype

#### List of Applicable Standards

The following is a list of two standards relevant to the structural subsystem. Both pertain to the insulation and its process of being properly applied to the system in accordance with national rules – ASTM stands for “American Society for Testing and Materials”. This organization is especially pertinent to Thermocline’s system, ensuring the team’s fabrication process, resources, and tools are all efficient, adhere to proper safety, and promote the success of the final product.

1. ASTM F1886: “Standard Test Method for Determining Integrity of Seals for Flexible Packaging by Visual Inspection”
2. ASTM C633-01: “Standard Test Method for Adhesion or Cohesion Strength of Thermal Spray Coatings”

#### Analysis

Based on the law of heat conduction, the thickness of insulation is a function of the insulation’s thermal conductivity ( k_(ins) ), surface area ( A_(sur) ), internal temperature ( T_(int) ), external temperature ( T_(ext) ), and the heat transfer rate ( Q_(cod) ) (Equation 1).

Δx_(ins) =(k_(ins) A_(sur) (T_(int) -T_(ext) ))/(Q_(cod)) (1)

In using estimated and expected values for each variable, the minimum insulation needed to maintain a safe-touch temperature of 50oC during heating is 0.095in (Equation 1).

Δx_(ins) =((0.036W/(m∙K))(810in^2 )(70^o C-50^o C))/(156W)[(0.0254m)/(1in)] (1)

Δx_(ins) =0.095in

The results of this analysis, albeit rudimentary and include numerous underlying variable/value assumptions, provide insight into critical layers of insulation needed throughout the system during heating operations. Cooling will require less insulation to maintain a safe-touch temperature as the temperature-difference between the internals and externals of the chamber will be smaller. These conclusions also assist the design of the chamber regarding the redirection of airflow in order to maintain temperature uniformity, arrangement of components, and the level of safety needed to be present – satisfying defined and ancillary requirements. The insulation design is to include a large factor of safety, with excess amounts of fiberglass insulation material used to protect internal components and hold a touchable external temperature. Ensuring no air gaps and tight seals conforming to the structure will reduce thermal leakage within the system, and uphold the level of safety desired by the team.

A critical analysis needed for the structural subsystem is also the total weight. For this directly influences operator usability and convenience, while also necessitating certain brackets, fixtures, and joints to maintain mechanical stability. Therefore, an analysis was conducted to explore the current best estimate (“CBE”) for the primary structural weight. The team used both property tools and direct measurements from Inventor and Onshape CAD to calculate the volume, converting this to weight given an approximated density of the material. The relevant formula was based on weight ( W ) being a function of density (ρ) and volume (V) (Equation 2). The results can be seen in Table 2.4.

W=ρV (2)

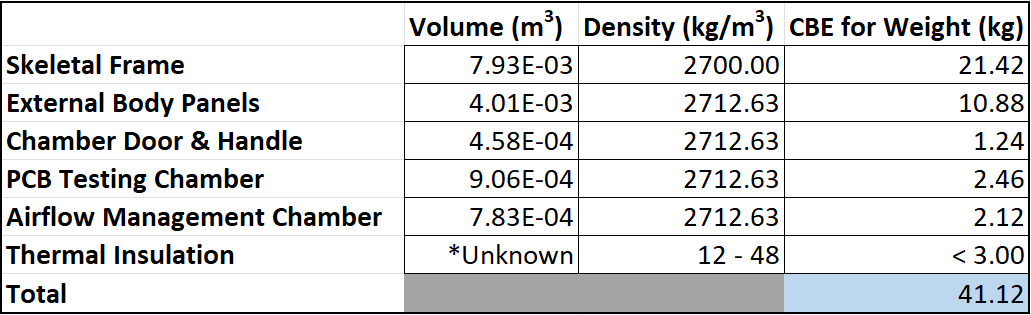
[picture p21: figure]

Table 2.4; Current Best Estimate for Structural Weight

### Component Design Detail

The design of the structural subsystem primarily consists of the body’s frame, body panels, alongside internal housings and external mechanisms. These constitute the assembly of the materials, components, and design specifications for the structure and its function. When fully assembled, the external view of the product appears to be a solid metal structure, roughly 22(in) by 31(in) at the base, and 24(in) tall. It consists of jointed panels, revealing only a mounted HMI display, chamber door, and the internal access of the PCB testing chamber, as shown in Figure 2.2.

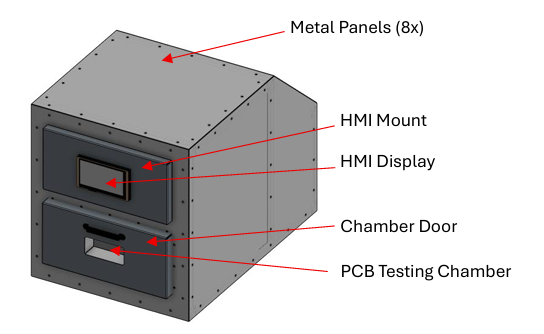
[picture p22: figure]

Figure 2.2: Chamber External Assembly

80-20 aluminum-extrusion parts make up the body’s frame – providing the “skeleton” for the system. These are strategically designed to not only support the structural loads and material stresses, but serve as attachment pillars for the external panels and insulation. L-brackets will connect these in the assembly in order to maintain their structural integrity and keep the system properly aligned. Several viewpoints are shown in Figure 2.3.

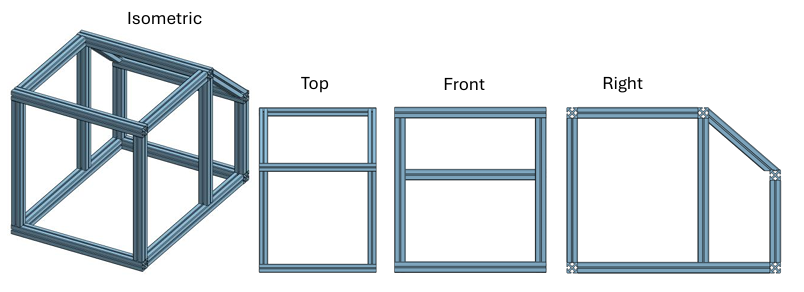
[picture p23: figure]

Figure 2.3: Frame Assembly Views

The 8 body panels, directly mounted to these frame pieces, consist of 6 external (left and right sides are duplicates) and 1 internal. All will be individually-cut from the Send-Cut-Send manufacturer, and are designed to provide easy installation and removal for necessary maintenance purposes. All panels will have laser-cut holes, allowing screws to mount the panel to the respective frame. Other holes are designed for “rivnuts” that connect to other components of the system; these joints are an integral part of the system, ensuring all structural connections are secure, able to withstand internal stresses caused by mechanical vibration, and can be easily attached to the thin Aluminum pieces which constitute most of the structural frame and body. All panels are shown in Figure 2.4.

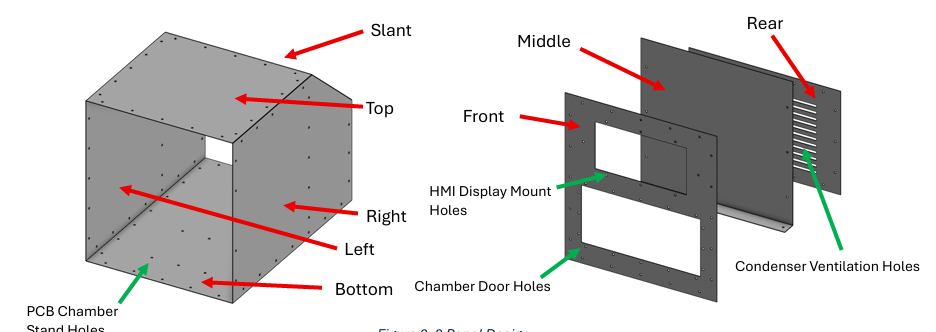
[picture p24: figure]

Figure 2.4: 8 Panel Design

The PCB testing chamber, mounted to the rear of the front panel, is outlined in Figure 2.5. There are 4 pieces, including 1 top, 1 bottom, and 2 sides. The parts will be made from the same material, and primarily due to the complex shapes, manufactured from Send-Cut-Send. They are designed for simple installation and maintenance. The chamber shall also have a subjacent “stand” serving for structural support and mitigation of vibrations during operation – mounted to the bottom panel.


Figure 2.5 PCB Testing Chamber & Support

The air management compartment redirects airflow throughout the PCB testing chamber, being mounted to the top, and is outlined in Figure 2.6. The 3-panel design consists of 1 front, 1 rear, and 1 top piece. This allows the respective personnel to have easy access to the internal components, while providing room for the thermal-fluid and electrical components to reach the rest of the system. These pieces will be fabricated with the same material and manufacturer described aforehand.


Figure 2.6: Airflow Management Compartment

The HMI Display Mount is to be fabricated with the same material and manufacturer, and mounted on the front panel. Its features were designed for aesthetics, ease of HMI-installation, and a proper cavity for all necessary electrical wiring to protrude from the back. The HMI mount is shown in Figure 2.7.


Figure 2.7: HMI Display Mount

The external door, shown in Figure 2.8, is to be made of 3 primary parts, including a front piece, rear piece, and handle. Each is to be fabricated with the same material and manufacturer. The door will be hinged to the front panel, ensuring a smooth opening-mechanism. There shall also be a glass window housed between the front/rear pieces to provide viewing access into the chamber, reducing the need to open the door mid-operation.


Figure 2.8 Chamber Door Handle Design

Last of all, fiberglass insulation fills most of the empty space in the system – within the panels – providing sufficient protection to satisfy the “proper thermal sealing” requirement for both chamber openings and components; this increases human safety, material longevity, and maintains proper system operation.

The structural subsystem, falling under the “mechanical” category of the product, focuses mainly on the intricates of the framework design, and its supporting impact for other subsystems. Its primary purpose is to maintain the integrity, alignment, and stability of itself and other components. Its design is made for efficient connections and organized integration of wiring that ensure a mechanically solid and highly functioning system; the support provides mounting points for fixtures and devices, maintaining positioning, solid connections, and mechanical stability during loading/unloading boards and reliability during PCB testing. It ensures a rigid enclosure for all heating/cooling elements and electronic components, promoting efficient dynamic functioning of other parts. Its secondary purpose is to be designed with proper material usage – ensuring long-lasting quality. A thorough material selection process enables the final structure to withstand thermal heat transfer rates throughout the system, protecting the integrity and performance of other components under natural environmental conditions. During operation, a well-built structural subsystem also reduces mechanical stresses encountered on other components by distributing and dampening loads uniformly, preventing deformation of other internal housings and connections. This ensures other subsystems operate effectively while maintaining safety and precision required for evaluating the performance of the PCB. Overall, the structural subsystem is an integral part of the entire system design, ensuring reliability in itself and other components, alongside high-performance of other subsystems. It is able to satisfy the requirements with a strategic design that accounts for external/internal dimensions (STR-01, STR-02), while also including proper thermal sealing for openings (STR-03) and necessary components (STR-04).

# Subsystem: Structural – Thermo-Fluid

### System Requirements

Table 3.1: Thermo-Fluid Requirements

### System Design

Trade Studies

Proof of concept or feasibility testing

List of Applicable Standards

Analysis

### Component Design Detail

# Subsystem: Safety

### System Requirements

The following section details the Safety Subsystem requirements and their compliance information. Requirements are grouped by category to align with system-level safety goals. Each table provides traceability between the requirement, associated rationale, applicable standards, and planned verification methods for PDR.

Table 4.1: Internal Safety Requirements

Number | Requirement | Rationale | Stand/Source | Verification Method | Status
SAF-01 | The internal surfaces shall be safe for electronics according to ASTM D3874-20 | Ensures internal chamber surfaces do not cause thermal or material degradation of sensitive electronics | ASTM D3874-20 | Test- Measure internal surface temperatures while chamber operates at maximum thermal load | Planned

Table 4.2: External Safety & User-Contact Requirements

Number | Requirement | Rationale | Standard/Source | Verification Method | Status
SAF-02 | External System surfaces shall not exceed the safe-touch temperature of 50°C per ASTM C1055 | Prevents user injury from unsafe contact temperatures during operation | ASTM C1055 | Test – Measure exterior surfaces at thermal steady-state during high temperature operation | Planned

Table 4.3: Operation & Fault-Response Requirements

Number | Requirement | Rationale | Standard/ Source | Verification method | Status
SAF-03 | The system shall be capable of operating in normal environmental conditions of 21°C. | Ensures reliable performance under expected laboratory ambient conditions. | System Environmental Requirements | Analysis/Test - Validate thernal stability and control while operating at 21°C ambient | Planned
SAF-04 | The system shall include a safety measure if internal temperature range or tolerance is exceed | Prevents overheating, thermal runaway, and hazardous internal conditions | System Safety Requirements | Test/Inspection - Induce fault condition and verify that safety mechanism activates as intended | Planned

Table 4.4: Safe-State Requirements

Number | Requirement | Rationale | Standard/Source | Verification Method | Status
SAF-05 | The system shall incorporate a defined “safe-state” that engages during abnormal or unsafe conditions | Ensures chamber transitions to a non-hazardous state to protect users and hardware | System Safety Requirements | Analysis/Test - Simulate fault conditions and verify that the system enters and maintains safe state | Planned

### System Design

While safety is a very important subsystem there was many overlaps in the Trade Studies we have done. S0 Although there is no trade study specifically in this section the insulation trade study is very valuable to consider for safety. It will help to determine the most suitable option to keep the chamber a resonable temperature to touch because the insulation will limit the amount of heat loss.

#### List of Applicable Standards

ASTM D3874-20

ASTM C1005

#### Analysis

The thermal resistance, R, is a function of the thickness of the insulation, L, divided by the thermal conductivity of the insulation, k. (Equation 4.1)

R=L/k

R=(0.1524m)/((0.032W/(m⋅K)))=4.76

R=(0.1524m)/((0.034W/(m⋅K)))=4.48

Where

L = thickness(m)

K = Conductivity (W/m*K)

I have used 2 different values because in the specifications of this material there was a range so I checked both sides of the spectrum for these values to get a range.

### Component Design Detail

The safety subsystem is integrated throughout the entire system rather than being represented by a single physical component. Its purpose is to ensure safe operation of the device under all expected environmental and load conditions by mitigating thermal, structural, electrical, and operational hazards. The safety design relies on coordinated interactions with the Structural, Thermo-Fluid, Electrical Components, and Control System subsystems to maintain safe limits, prevent equipment damage, and protect personnel.

##### Interface With Structural and Thermo-Fluid Subsystems: Insulation and Safe-Touch Temperature

A primary safety feature is the installation of thermal insulation, which provides a barrier between hot internal components and the external structure. The insulation physically interfaces with the structural subsystem by attaching directly to the interior surfaces of the housing. Structurally, the insulation must comply with thickness, compressive strength, and mounting constraints, ensuring that it does not interfere with internal clearances or cause deformation of panels.

From a safety standpoint, the insulation ensures the external surface temperature remains within safe-touch limits. This prevents burn hazards and reduces the risk of unintentional thermal exposure during handling or maintenance. The thermo-fluid subsystem provides the heating and airflow conditions which determine internal temperatures; the insulation enables this subsystem to operate effectively by limiting heat loss, controlling thermal gradients, and maintaining predictable external temperature profiles. Together, the insulation and thermo-fluid subsystem form a coupled safety barrier that protects users while preserving structural integrity.

##### Interface With Electrical Components: Current Transformer for Electrical Protection

The safety subsystem also interfaces closely with the electrical components through the inclusion of a current transformer (CT). The CT is used to monitor real-time current draw from critical components. Its primary safety function is to detect abnormal electrical conditions—such as overcurrent, short circuits, or unexpected load spikes—that could generate heat, damage components, or create fire hazards.

Figure 4.1: Current Transformer

The CT sends continuous current measurements to the electrical subsystem and, more importantly, to the control system. When the sensed current exceeds a predefined safety threshold, the CT enables the system to trigger protective circuitry, initiate controlled shutdown procedures, alert users through system indicators, and prevent overheating in wiring or power electronics. Because electrical faults are often precursors to thermal or structural hazards, the CT acts as a key interface point linking electrical safety to the overall system health. It ensures compliance with safety limits and provides the data necessary for automated protective actions.

##### Interface With Control System

The control system integrates all safety data including temperature readings, CT feedback, and environmental monitoring into a unified logic framework. It uses these inputs to enforce safety rules, initiate alarms, and command subsystem shutdowns when necessary. This makes the control system the enforcement mechanism for the safety subsystem’s requirements.

# Subsystem: Electrical Components

### System Requirements

The electrical components subsystem contains six requirements, including rules dictated by NEC (National Electrical Code) and UL (Underwriters Laboratories), as well as requirements per the project.

Table 5.1: Electrical Components Requirements

Number | Requirement | Rationale | Standard/Source | Verification Method | Status
COM-01 | The PCB shall be operatable while temperature is controlled | Ensures the electronics under test can function reliably during thermal testing without interruption or damage due to active temperature control | System ConOps; Functional Performance Requirement | Measure (Demonstration) | Planned
COM-02 | System will adhere to NEC rules on grounding according to Article 250 | Proper grounding reduces the risk of electric shock, equipment damage, and fire hazards, ensuring safe operation for users and equipment | NEC Article 250 | Inspection | Planned
COM-03 | System will adhere to NEC rules on appropriate fuses and load wire sizes | Correct fuse ratings and conductor sizing pretext the system from overcurrent conditions and prevent overheating or fire. | NEC (Overcurrent Protection and Conductor Sizing Requirements) | Inspection | Planned
COM-04 | System will adhere to UL 61010 for test and measurement equipment | Compliance ensures the system meets recognized safety requirements for laboratory and test equipment operation | UL 61010 | Inspection | Planned
COM-05 | The sensors shall be properly rated to withstand internal environment conditions. | Ensures sensor accuracy, reliability, and longevity when exposed to expected temperature ranges inside the chamber | Manufacturer Datasheets; System Environmental Requirements | Inspection | Planned
COM-06 | The system shall support PC connection for datalogging | Enables data collection, analysis, traceability, and verification of system performance during testing | System ConOps; Data Logging Requirements | Inspection | Planned

### System Design

#### Trade Studies

The primary trade study for this subsystem is the heating element. A trade study was conducted via four possible options:

Table 5.2: Heating Trade Studies

| Resistive | Inductive | Convection | Reversible Heat
Description | Current Passes through a resistive element which converts energy into heat through the element’s resistance | A quickly alternating magnetic field that induces eddy currents | Transfers heat through circulating air/fluid, heated by resistive elements. | Add a reversible heat valve to allow recycling heat from the thermal hot side for use in heating.
Price | ~$100 | ~$800 | ~$600 | ~$500
Risk | Overheating/fire hazard | Electromagnetic Interference (EMI)/ magnetic fields | Temperature non-uniformity/runaway airflow heating | Adds failure points to the thermal system, risks overheating the oil.

Proof of concept or feasibility testing

For testing, the relays with the flyback protection were breadboarded to ensure that the design worked as is intended.

List of Applicable Standards

IPC-2152

Analysis

To calculate the proper trace width when designing the PCB, four equations were used:

Current Carrying Capacity, where I is the allowable current, k=0.048 for external layers, is the allowable temperature rise, and A is the trace cross-sectional area (width * copper thickness).

I_(cc) =k⋅(ΔT)^0.044 ⋅A^0.75 (1)

Trace Width, where W is the required trace width, and t is the copper thickness.

W=A/t (2)

Trace Resistance Analysis, where R, is the trace resistance. Ρ is the resistivity of copper 1.72⋅10^(-8) Ω⋅m , L is the trace length, t is the copper thickness, and W is the trace width.

R=p(L/(t⋅W)) (3)

Trace Heating/Performance Margin, where ΔT is the temperature rise of the trace and, I is the current through the trace.

ΔT=0.024⋅I^1.6 (4)

The power traces supplying the relay coil and fans were sized using IPC-2152 (Institution for Interconnecting and Packaging Integrated Circuits) current carrying capacity guidelines. Equation 1 provides the trace current limit as a function of copper cross-sectional area and allowable temperature rise. An allowable temperature rise of ΔT= 10°C is reasonable as the thermal chamber operates over a wide temperature range (-40°C to 85°C), this also ensures that at the extreme case (85°C), the copper, solder joints, and connector plastics remain under 95°C, which is within IPC guidelines material limits and helps to improve longevity. The resulting required trace area is now converted to trace width using equation 2 assuming 1oz Copper (0.35 μm thickness). Equation 3 is used to check that the resulting trace width and Voltage drops are acceptable for relays and fan loads. Equation 4 is used to confirm that the expected operating current does not exceed the ΔT margin. Based on these calculations, it was determined that the trace widths should be approximately 8mm, with a maximum current carrying capacity of 12-15 amps.

### Component Design Detail

The role of the electrical components subsystem can be understood through the flow chart in Figure 5.1:

Figure 5.1: Electrical Flowchart


The electrical components subsystem consists of a PCB that provides control and communication throughout the thermal testing chamber. The primary controller is a Raspberry Pi Pico which interfaces with four thermocouple drivers which are used for temperature measurement. The subsystem design, shown in Figure 3, includes relays, a BJT, op-amps, current sense transformers, indicator LEDs, a DHT11 humidity sensor which will be a standalone component, not on the PCB used to measure humidity in the chamber, and an IRM used as the analog-to-digital converter. The interconnect board, shown in Figure #, allows the PCB to talk to the HMI to transmit data to the user.

Figure 5.2: Interconnect board


As of most recent updates, the PCB stands as shown:

Figure 5.3: Current PCB Layout


The functional role of the PCB is to monitor the internal temperature of the chamber and communicate that data to the HMI. It continuously reads temperature, humidity, load conditions, and provides the necessary control for the heating and cooling elements.

# Subsystem: Control System

### System Requirements

Since the software is so broad reaching in the system, many different requirements fall under its roof, including safety, control, power and interfacing.

Table 6.1: Customer/System Requirements

Number | Requirement
CST-1.1 | The system shall include a Human Machine Interface (HMI) for the control system
CST-1.2 | The system shall include separate operating/control modes.

Table 6.2: Control System Requirements (Part A)

Number | Requirement | Rationale | Standard/Source | Verification Method | Status
COM-06 | The system shall support Personal Computer (PC) connection for datalogging | Enables users to collect, store, and analyze test data for performance verification, traceabilitiy, and reporting purposes | System ConOps | Inspection | Planned
CON-01 | The system shall allow local temperature set-point control | Provides users with direct on-site control of chamber temperature to support setup, calibration, and manual testing operations | System ConOps | Test | Planned
CON-02 | The system shall allow remote temperature setpoint control | Allows users to control chamber temperature remotely, iimproving usability, safety, and operatoinal flexibility during testing | System ConOps | Test | Planned
CON-04 | The system shall prohibit thermal control when teh chamber door is open | Prevents unsafe operating conditions, reduces risk of user injury, and protects hardware from unintended thermal exposure | System ConOps | Demonstration | Planned
CON-05 | The system shall prohibit thermal control when a user is handling the Printed Circuit Board (PCB) | Ensures user safety and prevents damage to the PCB by disabling thermal control during direct user interaction | UL 61010 | Demonstration | Planned
CON-06 | The system shall log temperature data | Allows verification of system performance over time and supports post-test analysis, troubleshooting, and documentation | System ConOps | Test | Planned

### System Design

Trade Studies

##### Screen Selection

To meet requirements CST:1.1, SAF:04 and CON:01, the HMI for the systems hall need to provide for both graphics and output, as well as numerical and configuration input.

Table 6.3: Control System Requirements (Part B)

Number | Requirement | Rationale | Standard/Source | Verification Method | Status
CON-07 | The system shall log humidity data | Enables monitoring and verification of environmental conditions that may affect PCB | System ConOps | Test | Planned
CON-08 | The system shall log faults for safety measures | Provides traceability of safely-realted events, supports troubleshooting, and enables verification of proper safety subsystem operation. | System ConOps | Measure | Planned
CON-09 | The system shall have a “shutdown” state | Ensures the system can be placed into a safe condition to protect users and hardware during faults, maintenance, ir emergency conditions | UL 61010 | Demonstration | Planned
CON-10 | The system shall have a “standby” mode | Allows the system to remain powered while minimizing active thermal control, improving safety, readiness, and energy efficiency | System ConOps | Demonstration | Planned
CON-11 | The system shall have a normal operating “start” mode | Establishes a controlled and repeatable transition into normal operation, reducing the risk of unsafe or unintended system behavior | System ConOps | Demonstration | Planned
CON-12 | The system shall allow for manual switching between modes | Provides user control and flexibiility during testing, setup, and troubleshooting while maintaining defined system states | System ConOps | Demonstration | Planned

No requirement mandates that the HMI be part of the machine. Therefore, we could satisfy the requirements by using off-board or external computer control. We considered this alternative in our trade study in Table 5. We quickly decided through the trade study that the most desirable HMI option would be something built into the machine itself, and among those two options, using a low-level interface was the most desirable and thus the selection we went with. We experimented with a few models and settled on purchased one for testing. As part of our initial verification experimented with a CrowPanel HMI screen “7 Inch HMI Touch Display- 800x480 LCD for ESP32/Arduino/LVGL”, 2023 shown in Figure 1. The screen is programmable in C and uses Light and Versatile Graphics Library (LVGL) for the Graphical User Interface (GUI). Our initial GUI design allows the major operating modes, configuration, and calibration to be separated by tabs along the top bar, with buttons in the center and live status, error, and safety warnings below Figure 6.1.

Table 6.4: Screen Selection Trade Study

| External Computer | LVGL UI | Internal Computer
Boot Time | N/A | Fast | Slow
Size | External device required | Small (under 7”) | Medium to Large (Over 7”)
Estimated ease of use | Low, WiIl require at least setting up site or software on user’s computer | Medium, all controls integrated and available quickly. LVGL may make animations, tooltips and other graphics somewhat basic | High, Full sized UI with as much complexity you like
Ease of integration | High, we don't worry about integration system-side. Push all the work off to software on a PC that isn't ours | Medium, more work on our end. Installation of a screen on the machine and simple graphics | High, we mut manage whole Operating Systems (OS) and graphics stack, as well as the graphics and control underneath
Ease if programming | High, use anything we like | Medium (embedded C/C++) | Medium, graphics are as easy as with an external machine but we must also manage the single board inside as well

Choosing an MCU was a similar process to choosing a screen. Both are crucial parts of the software stack as the controller and display (Table 6 and Table 7) are what will allow the software to run at all. Our trade study took into account how easy it would be to integrate and use the MCU, but also what safety features were offered, what support was available and how expensive it would be to re-tool or replace. In the end, we selected using the RP2040. Having a solid core with good safety systems and easy integration was the most important and met the requirements best.

Figure 6.1: CrowPanel 7.0 ESP32


Figure 6.2: Thermocline GUI Prototype, LVGL block


##### State Machine

A good portion of our design centers around the safety and discrete modes the system can operate in. This is one of the reasons supporting a good Real-Time Operating System (RTOS) was so critical in our selection of an MCU (Table 6.5 and Table 6.6). To this end, our system has several modes, all of which have safety background tasks, control systems tasks, user interface tasks and other functions dependant on the mode you’re in or the mode you’re transitioning to.

Table 6.5: MCU Trade Study (Part A)

Criteria | CRIO (NI) | RP2040 | Arduino (AVR) | Arduino (SAMD) | ESP32
Cost | Very High $2,500 | Very Low <$40 | Low ~ $40 | Very Low < $40 | Very Low < $40
Integration | Low, LabView might be easier to develop on but harder to port (and meet Req COM:06) | Very easy, Integration with python, JavaScript Object Notation (JSON) and Universal Serial Bus (USB) | Easy, Integration over serial | Very easy, full USB stack, python, JSON | Easy, integration over serial
Safety Features | Physical hardware safety features like Electromagnetic Interference (EMI) Electrostatic Discharge (ESD) but limited software ones | Hardware watchdogs, Memory debugging, EMI/ESD | Hardware watchdogs, EMI/ESD | Hardware watchdogs, Memory debugging | Hardware watchdogs, Memory debugging

Figure 3 is a flowchart detailing each state the machine can be in. The primary states are:

- Power-On Self-Test (POST): Power on and self test
- Safe Mode: Safe return mode where the suer can examine an error or reset to a known state with all functions in idle or disabled
- Standby: Default standby mode, await user input and allow to move to any other mode
- Configure: Configure the system, make adjustments and view information before or after use
- Follow Curve: Follow a curve, change the chamber setpoint automatically according toa a script, curve or chart
- Follow Setpoint: Follow a setpoint, change the chamber setpoint to a specific value and hold there.

Table 6.6: MCU Trade Study (Part B)

Criteria | CRIO (NI) | RP2040 | Arduino (AVR) | Arduino (SAMD) | ESP32
RTOS | Yes (But only NI Linuz RT) | Yes (any) | No | YEs (Zephyr and Free Real-Time Operating System (FreeRTOS)) | Yes (FreeRTOS)
Support | Yes (Via NI) | Yes (Most Vendors, RPi, Adafruit) | No (Phasing out) | No (Obscure) | Yes (Some vendors, Esprissif, Adafruit)
Input/Output | Good, Expandable Digital Analog Converter (DAC) and analog-to-digital converter (ADC) operations (at a price) | Good, great General Purpose Input/Output (GPIO) and Programmable Input/Output (PIO) system, only a limited set of analog pins. | Limited poor resolution ADC and limited pin counts and specialized pins | Good, robust ADC and many GPIO on most chips | Good, passable ADC pin counts for most models

Figure 6.3: Thermocline State Machine


We don’t want to reinvent the wheel; an RTOS on a microcontroller is a common and well-understood task management solution. We chose to use FreeRTOS (“FreeRTOS™- FreeRTOS™”, n.d.) for our system as it allows for easy task creation and management. Tasks will be structured to run on a priority system, where tasks that are checking for safety conditions (such as overtemperature, interlocks, overcurrent, undervoltage, etc.) will preempt other tasks running, or cancel them entirely. This RTOS operation also allows ”background” tasks to run periodically, and perform low-priority items such as updating the display, syncing the time, saving the data.

Figure 6.4: Overview of Task State Management


Proof of concept or feasibility testing

#### List of Applicable Standards

#### Analysis

### Component Design Detail

#### Intercommunications

The central software controller stack will include both the built in screen, as well as a potential customer computer. To simplify the amount of work we need to as programmers, and the work the system needs to do in computation, the interconnect language will be the same for both. JSON is a common language for intercommunication between systems, and is a good fit for our needs. By encapsulating the data in JSON objects, we can easily send and receive data between one or more systems, as well as assign types, instructions and names to each packet. Such packets may look like Figure 6.5.

Figure 6.5 Example JSON Packet


#### Sensors and Inputs

Computers don’t come with an awareness of their environment so we need to integrate our own. The implementation of which is largely an electrical one, but what we do with those sensors is all in software. There are two main responsibilities turned over to the software, one is actually reading the data and reacting in a timely manner, the other is pro cessing, filtering and presenting the data. One consideration is under- or oversampling. The analog system on our control board will provide as much data as we need, but once we sample it we could be undersampling and alias ing noise. The mitigation of this example can be found in subsection 6.1. For the storage and presentation of the data, we need to consider what rate is necessary for the storage and what rate is appropriate for the pre sentation. The customer may prefer to see a significant resolution in their saved data, but what is shown on the screen may not benefit from a very high update rate. In fact, oversampling could make the screen flicker or look sluggish. The software will balance what data it sends and at what rate, and allow different rates internally.

#### Drivers and Outputs

The most critical job of the software is at the very end, the end-effector. The product of the control system is to set, unset and toggle various relays, drivers and devices that will do meaningful and potentially dangerous work. Relays have a finite lifespan, arcing across the contacts as well as me chanical wear from cycles will affect their life and the performance of their switches. The software must self-regulate and prevent overuse of the relays. In addition, there are many more loads controllable by the system than the power budget allows for. The software will need to never exceed the power budget and it must keep track of which loads are running and not cycle incompatible loads on at the same time.

Figure 6.6: Example of electrical arcing across relay contacts. Source: Wikipedia


# Risks and Mitigation

Table 7.1: Risk Matrix


Figure 7.2: Risk Vs. Likelihood


Figure 7.3: Most severe risks and mitigations.


# Verification Matrix


Table 8.1: Verification Matrix

# Design Considerations

#### Global Considerations

The system design reflects awareness of global impacts related to material sourcing, manufacturing practices, and energy usage. Aluminum alloys were selected for structural components due to their abundance, recyclability, and relatively low environmental burden. Manufacturing methods were chosen to minimize material waste and promote responsible supply chain practices. Energy efficiency was also considered across thermal control, insulation, and software logic to reduce overall power consumption in alignment with global sustainability goals.

#### Cultural and Social Considerations

While the system does not directly interface with culturally sensitive applications, its design emphasizes universal usability and accessibility. The chamber is ergonomically designed for ease of operation, with dimensions and interfaces that accommodate a broad range of users. Safety indicators, warnings, and operational cues rely on intuitive symbols and clear visual feedback rather than language-specific instructions, reducing cultural and language barriers. These choices promote safe and inclusive interaction in diverse laboratory environments.

#### Public Health, Safety, and Welfare Considerations

Public health and safety are central to the system design. Structural materials and insulation prevent hazardous external temperatures and eliminate sharp edges or unsafe protrusions. Electrical safety is ensured through proper grounding, fusing, relay isolation, and PCB trace sizing in accordance with industry standards. Temperature and current sensors, combined with automated Safety Mode logic, prevent runaway heating, electrical faults, and unsafe operating conditions. Interlocks disable thermal control during unsafe states, protecting users, equipment, and the surrounding environment. These measures fulfill ethical responsibilities to safeguard users and the public.

#### Economic Considerations

Economic efficiency was balanced with safety, reliability, and performance. The use of repeated structural components reduces fabrication and assembly costs. Material selections were optimized to provide durability and long service life, minimizing maintenance and replacement expenses. Cost-effective electrical protection components prevent catastrophic failures and reduce downtime. Energy-efficient insulation and control logic further reduce operational costs, resulting in a system that provides strong long-term value and return on investment.

#### Environmental Considerations

Environmental impact was addressed through sustainable material selection, energy efficiency, and long-term system durability. High-performance insulation minimizes heat loss and reduces power consumption. Control software limits unnecessary operation and reduces energy usage during fault conditions. Structural design minimizes the likelihood of thermal-fluid leakage and reduces waste by extending component lifespan. Together, these design choices reduce environmental impact, conserve resources, and support sustainable engineering practices.

# Open Design Issues

- Chassis
- Shocks/Vibration Dampening
- Pre-Final Sheet Metal (Laser Cutter)

# Budget

Table 11.1: Itemized Purchased Budget

Table 11.2: Overall Budget


# Conclusion

The thermal testing chamber is comprised of 5 major subsystems: structural, thermo-fluid, safety, electrical components, and software. (https://team-thermocline.github.io/)

# References

1. OpenAI (2025) ChatGPT v5.0 https://chatgpt.com/chat prompt: “What are some design considerations I should take into account when designing PCB traces?” (with edits)

2. RayMing. (2025, May 14). IPC-2152 Standard: PCB Trace & Via Current Calculator, Free PDF Download, and Design Guidelines https://www.raypcb.com/ipc-2152/

3. HTY. (2025). Copper Trace in PCBs: Everything You Need to Know. https://www.pcbasic.com/blog/copper_trace.html

4. Jhdpcb. (2023, June 19). The Ultimate Guide To PCB Trace Width Calculator https://jhdpcb.com/blog/pcb-trace-width-calculator

5. Trace Resistance Calculator. (2016, April 20). https://www.allaboutcircuits.com/tools/trace resistance-calculator/

6. 7 Inch HMI Touch Display- 800x480 LCD for ESP32/Arduino/LVGL [Sec tion: products]. (2023, June). Retrieved November 20, 2025, from https://www.elecrow.com/esp32-display-7-inch-hmi-display-rgb-tft lcd-touch-screen-support-lvgl.html

7. FreeRTOS™- FreeRTOS™. (n.d.). Retrieved November 20, 2025, from https: //freertos.org

8. Richter, A. (n.d.). The Anatomy of a 3D Printer: Screens. Retrieved Novem ber 20, 2025, from https://www.matterhackers.com/articles/3d printer-anatomy-screen

9. Standard Test Method for determining integrity of seals for flexible packaging by visual inspection. (n.d.). https://store.astm.org/f1886_f1886m-16.html

10. Standard test method for adhesion or cohesion strength of thermal spray coatings. (n.d.). https://store.astm.org/c0633-13r21.html

11. Sendcutsend.com. (2025, October 29). 5052 Aluminum Laser Cutting | SendCutSend. SendCutSend. https://sendcutsend.com/materials/5052-aluminum/#063-bend-specs

12. OpenAI (2025) ChatGPT (GPT-4o) https://chat.openai.com/chat prompt: “How to make this table into a word appropriate table?” with edits

13. ASTM. (2019). ASTM International - Standards Worldwide. Astm.org. https://www.astm.org/

14. https://energycompliance.com.au/what-is-thermal-conductivity-of-different-insulating-materials/?utm

15. Amir, & Amir. (2020, September 17). Thermal properties of insulating materials - Energy Compliance. Energy Compliance. https://energycompliance.com.au/what-is-thermal-conductivity-of-different-insulating-materials/?utm

16. Basso, E. (2024, December 2). The Ribbon 6. AIS Group. https://www.ais-group.com.au/blog/insulation-thermal-conductivity-and-r-value/?utm

17. K-Value, U-Value, R-Value, C-Value. (2017, June 9). Insulation Outlook Magazine. https://insulation.org/io/articles/k-value-u-value-r-value-c-value/?utm

Page | 1 EG498 Capstone Design I

Thermocline, CDR

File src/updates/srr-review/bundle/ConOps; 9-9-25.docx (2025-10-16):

EG-498-10342/10351 Capstone Design I

Report: Concept of Operations

Date of Submission: 09-17-2025

Authors: Nikolai DiLullo, Alexandra Friebolin, Alexia Hnatowicz, Jacob Morrissette, Joseph Sedutto


Instructors: Professor Jennifer McInnis & David Guo

Sponsor: Professor Monk

School of Engineering, Technology, and Aeronautics


Contents

# 1 Introduction

A Concept of Operations (referred to as “ConOps”), is a complete, thorough, and technical description of a system—oftentimes including illustrations for a visual understanding. It clearly defines the system’s operation, environment, application, purpose, and associated risks. The information in the ConOps should be easily translatable into system and subsystem requirements that promotes effective analysis, a versatile, reliable, and optimized engineering design. The primary descriptive areas are as follows:

- System Description
- Physical Environment
- Support Environment
- Operating Modes
- Use
- Stakeholders
- Impact Considerations
- Risks

# 2 System Description

This proposed system is a thermally-controlled Printed Circuit Board (“PCB”) testing chamber. It is a table-top system strategically designed for ease of use and versatility. The diverse array of mechanical, electrical, and software components work systematically to regulate and maintain precise internal thermal conditions, while electronic devices are tested for performance.

The PCB is inserted into the chamber, which houses the component during thermal changes and electronic testing; the chamber is designed to accommodate 12” x 12” electronic boards, and spans the commercial temperature range of 0oC to 70oC. Insulation minimizes undesired thermal loss across the internal refrigeration system and external seals/ports/doors. All system “entrances” allow for the insertion of the PCB and necessary power/data electronic cables, alongside maintenance purposes.

A user will then interface with the system (either locally or remotely) to set parameters and target values, and modify existing settings. Internal temperature data and control system performance are actively measured, logged, and stored in a text-based format for traceability, analysis, and maintaining a strict 3oC tolerance on the designated setpoint.

PCB testing procedures commence after the temperature setpoint has been reached and during its control. A successful product includes PCB functioning properly during temperature stabilization. This testing is used for verification and modification of electrical performance of PCBs and individual components.

Ultimately, this thermally-controlled PCB testing chamber enables engineers to simulate real-world settings, typical environmental conditions, and normal operating use-cases of electrical components. The performance results and analysis help to engineer improvements for more efficient, reliable, and capable systems.

# 3 Physical Environment

The physical environment consists of the necessary conditions for successful operation of the system.

The system will be operated indoors. It will not be designed for outdoor use where environmental factors are variable, such as extreme rain, wind, snow, or foreign debris; these may inhibit operation and performance characteristics of internal and external electronics, mechanical components, and other critical surfaces. External ports/openings/seals alongside the electromechanical devices will not be engineered specifically to withstand these conditions. Thus, the operation shall consist only in a predictable indoor environment. Access to ventilation is required for high quality performance, and meeting engineering codes. Laboratory ambient temperature conditions (approximately 20-25oC temperature and <50% humidity) are suggested for human safety, ease of maintenance, and long-lasting component performance, protection, and reliability.

Successful operation necessitates no specific lighting conditions, where the system can be used day or night.

Normal operation requires a consistent source of power for all sub-systems to successfully function, and a healthier system in the long-term.

A PC will be used for the collection of system information from the datalogger. The system will be designed for having one or more simultaneous operators with these controls. The user(s) can locally interface with the system through a built-in HMI device, or control the system remotely through the PC.

# 4 Support Environment

This section focuses on the additional resources, services, and conditions needed to operate, maintain for reliability, and support the system across its entire lifecycle. Individual parts and the whole system are designed and fabricated with replaceability, upgradability, and serviceability in mind.

For one, the system shall be designed with proper/clear maintenance access. This is important for faster/simpler routine inspections of electrical and mechanical sub-systems, cleaning procedures, calibration of components and systems, and replacements of materials and parts. Adequate space provides ease-of-access for personnel and materials during work.

Proper maintenance tooling and equipment are to be readily available within the indoor environment to ensure operation and testing are efficient and successful.

The required indoor electrical supply matching the system’s requirements is to support the system’s normal operation.

The mechanical design, electrical schematic, bill of materials, and other ancillary specifications are to be included with the chamber’s use and to be referenced for future support.

All components, systems, and fabrication techniques are to conform with contemporary standards.

# 5 Operating Modes

Power with solid fill

- The system will include a “Shutdown” state, where it’s fully disconnected and consumes no power. This will contribute to energy savings, while promoting longevity of components and materials.

Stopwatch with solid fill

- The system will have a “Standby” mode. Herein shall the system be powered on but performing no function. It will wait for user-input and configuration for safety purposes and ensuring the system operates as intended.

Wireless router with solid fill

- The system will have a “Start” mode. The various sensors, devices, mechanisms, electronic components, and software shall operate according to the temperature setpoint as specified by the user. This is the normal operation for testing the PCBs.

Warning with solid fill

- The system shall include a “Safe” state. With this, all mechanisms become manual allowing operators to safely investigate system errors, mechanical or electrical faults, or other issues pertaining to the system’s function and performance.

# 6 Use

The system will be used indoors in a laboratory setting to test PCBs under controlled thermal conditions.

A user(s) will insert a PCB (up to 12” x 12”) inside the chamber, connect the necessary electrical stimulus/measurement cables through the designated ports, and interface with the system to ensure conditions match the testing needing to be done. The target temperature setpoints via the HMI or remote PC control will be set. The internal chamber’s temperature and other data will be monitored real-time, and the user(s) will make the necessary adjustments as needed. Temperature information and the system’s status is logged to a PC. The effects on the PCB are to be observed.

The user(s) is responsible for loading/unloading the PCBs safely, initiating tests, setting the designated parameters, reviewing logged data, analyzing system performance, and making modifications as needed.

# 7 Stakeholders

Based on the system’s various use cases and engineering design lifecycle, it’s important to recognize all associated users and stakeholders. It will be designed for a variety of personnel that rely on it for testing, analysis, and engineering improvements, all who interact with the system in different ways.

- Primarily, “engineers” are responsible for the system’s outline, requirements, design, schematics, materials/resources, fabrication process, testing, analysis, and final product implementation. They are also the users who manage the actual operation of the system in regards to setup, software interfacing, and PCB performance verification. They ensure the entire design is up to specifications and meets the customer’s defined requirements.
- Some overlap with these stakeholders are “maintenance personnel”, who are responsible for maintaining the integrity of the system, sufficient resources, necessary tooling/equipment, appropriate electrical/mechanical/software inspections, and ensuring the system’s long-lasting performance. Oftentimes the engineers are the same ones responsible for maintaining the system.
- We are also stakeholders in our own project, completing our own project takes our own time to design, test, develop. And failure to meet the project’s milestones will reflect poorly on us as a team a well as individually, academically.
- Other primary stakeholders include the faculty and sponsor who play a direct role in providing project guidance, customer-driven requirements, while ensuring the correct resources are available and the project schedule is met.
- Some secondary stakeholders include possible faculty, students, electronic or thermal-based product manufacturing companies, society, and other personnel who use this system for personal engineering tests or project/product inspiration.
- Other companies that supply materials or fabrication tools are also stakeholders in this project. These, while having no hands-on application with the product in regard to control or designing the system, still play a critical role. They ensure proper lead-times, correct resources are shipped, materials are of high-quality, and thus the system’s design meets standards and specifications, which all help the project timeline to be accurately and efficiently followed.

Collectively, all of these stakeholders ensure that the thermally-controlled PCB testing chamber is efficiently developed, functions correctly and produces reliable data, and ultimately helping to accurately test/improve PCB performance.

# 8 Impact Considerations

The following impact considerations illustrate the possible situations the system can be subject to.

- Surfaces (primarily external) may extend beyond the safe-touch limits concerning extreme temperatures, having risk of accidental human injuries during or post-operation.
- Failure to implement proper electrical wiring and safety measures could increase the risk of electrical shock, human injury, fire hazards, and damage to internal electro-mechanical components.
- With inadequate ventilation, system may cause overheating to components or surroundings.
- Excessive system usage may cause high power consumption.
- Operating mechanical equipment may generate noise that can affect surrounding personnel or equipment.
- Insufficient table space or clearance could limit proper operation, restrict maintenance access, and increase the likelihood of accidental damage or safety hazards.
- The system may require extra personnel for regular calibration, cleaning, or inspection.
- Data collection may require constant management of storage space.
- System may need a user present for a safety measure prior to operation.
- Non-compliance with electrical safety or mechanical design codes or using improper materials for the system’s application could result in safety hazards, equipment failure, or unsafe operating conditions.

# 9 Risks

The risks associated with the system’s engineering design process, fabrication timeline, and normal operation are often identified as situations where the system doesn’t meet the predefined requirements. These risks help describe failure possibilities of the system, sub-components, materials, or other project facets.

On top of this, a thorough analysis of the system helps to foresee other issues that may not be evident from solely observing the requirements. Obtaining “sufficient analysis” is vitally important in ensuring an effective product design, efficiency in building, good resourcefulness, and a healthy system in the long-run.

To reach a “sufficient” amount of analysis, it should consider the product’s design, application, general function, and systematic integration – though this process may be time, cost, and resource intensive. This helps ensure a strategically designed product that not only satisfies the defined requirements but is inclusive enough to also consider situational variables – which are other factors that influence daily operation.

That is to say, sophisticated and profitable analysis that provides insights into the system’s risks, covers the “obvious” requirements (what the final system includes), while also providing design implications which concern the methods of engineering the final product (how the system is built, operated, and maintained).

With that being said, the proposed system was strategically analyzed to identify numerous diverse risks. These risks are grouped by categories that outline the entire system. They also are individually ranked by both likelihood (probability of occurrence) and consequence (severity of impact on the product or stakeholders). It’s important to note that the likelihood is not based on probability within the pool, and how likely a scenario is to occur compared to the other risks, but on an individual scale; there is a linear scale translating percentage (0-100% likelihood) to score (1-5). The final ranked score considering likelihood and consequence is categorized by severity using the 3 M’s (minor, moderate, major). From this, the higher-ranked risks are prioritized to redirect resources and effort, and the other risks – while still meaningful to the project and important for the system’s function and product success – are simply considered with less priority. Mitigation steps are initiated and tracked to reduce the risk score through design changes, preventative measures, or control plans.

The following figures highlight this system’s defined risks in the engineering processes of design, fabrication, analysis, redesign / optimization, final product development, installation, operation, and maintenance:


Risk List

Risk Matrix

Consequence | 5 | B, L | A, E, P | K, M, O | Z
| 4 | | Y | N | I | Q, W
| 3 | | F, G | T, U, X | V
| 2 | R | J | | C, D | H
| 1 | S
Combined Risk Scores - 0-9 Minor - 10-19 Moderate - 20-29 Major | 1 | | 2 | 3 | 4 | 5
| Likelihood

SNHU School of Engineering, Technology and Aeronautics (SETA) IDE Building, 2500 North River Rd. Manchester, NH 03106 Page 12

SNHU SETA REPORT Date: 09-17-2025 EG-498 ConOps Instructors: J. McInnis, D. Guo

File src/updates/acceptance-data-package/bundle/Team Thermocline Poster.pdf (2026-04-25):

## Purpose of a Thermal Testing Chamber

## Our Design Process

The team uses tools such as Autodesk Inventor, FreeCAD and Onshape to collaborate and design the chamber in 3D. The testing chamber is made from stamped and bent laser cut sheet metal parts and aluminum extrusion. The chamber is assembled with rivets, bolts and welds.

The body of the chamber keeps the user safe from extreme temperatures, hazardous insulation, and refrigerant.
In industry, thermal testing chambers are used to verify the operation of electronics and devices at various temperature ranges.

View our CAD,
documentation,
design process and
more on our
website!

We used SendCutSend for the manufacturing of the sheet metal parts. Parts arrived laser cut and bent to our CAD specifications. We assembled them after arrival using rivets, RTV silicone, rivnuts, and other fasteners and gaskets.

## Fabrication

Photo Credit LIBtest.com

KiCad was used to make the mainboard PCB and other
test or adapter PCBs.

JLCPCB was used as the manufacturer for the printed circuit boards, we rendered manufacturing files and had them shipped out. Shipping from China can take a while, so we always factored in lead times when ordering parts. Blank boards arrive in the mail and are assembled at SNHU by hand. We used LCSC as a parts supplier.

Joe Sedutto

Electrical
Engineer

About the Team

Testing chambers aid in verifying individual components and products function in many environments. They can also be useful for specific heat and thermal testing in other areas, such as unique materials, freeze-drying, and many applications.

Scan for CAD!

The team had both mechanical and electrical review processes, where we asked educators and industry engineers for input on our designs before sending them off to be made!

Scan for
schematics!

## Our Project

We are a team of engineering students at Southern New Hampshire University completing our capstone project. We are one of two teams making a thermal testing chamber this year!

Alexandra
Friebolin

Mechanical
Engineer

Jacob
Morrissette

Mechanical
Engineer

Nik
DiLullo

Electrical
Engineer

Alexia
Hnatowicz

Mechanical
Engineer

## Refrigeration System

Charged with 1lb of R410A, the system is around 2000cc internal volume. The absolute boiling point of R410A is –43C (-45F) at vacuum. We exploit this property by using 10ft of capillary tubing to restrict the flow much more than a normal refrigeration system.

Category | Type | Count
Frame | Aluminum Extrusion | 28ft
| Aluminum Panels | 25ct
Fasteners | Bolts | >250ct
| Rivet Nuts | 100ct
| Pop Rivets | 50ct
Thermal | Copper | 10lb
Denim Insulation | Denim Insulation | 5ft³

## Final Results

With evaporator temperatures nearing –36C (-32F) we've been able to meet all functional requirements related to temperature, ramp-rate and cycle time! With our current best minimum sustained air temperature at –27C (-17F).

Specification | Result
Minimum Air Temperature | -27C (1.5F)
Maximum Air Temperature | 75C (167F)
Maximum Cooling Ramp Rate | -1.5C/min
Maximum Heating Ramp Rate | >5C/min

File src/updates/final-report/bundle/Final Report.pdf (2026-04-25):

## Final Design Report EG-499 Engineering Capstone II


Alexia Hnatowicz, Jacob Morrissette, Joe Sedutto, Nik DiLullo, Alex Friebolin

Southern New Hampshire University April 24, 2026

Abstract:

SNHU’s final capstone course required students to collaborate across engineering disciplines to design, fabricate, test, analyze, optimize, and present a working product that satisfied customer requirements. Each student brought their unique mechanical and electrical experience to help develop the final product: a thermally-controlled PCB testing chamber that delivered efficient and highly successful performance. Team Thermocline was originally presented with several driving requirements provided by the customer – an electrical engineering professor, which described product dimension, function, and performance criteria. From this, the group developed a conceptual design, including materials, components, control features, and the expected assembly integration process. Trade studies were then conducted across the project, supported by external consultations with engineering, HVAC, and manufacturing/machining professionals to approve – or improve – the product design. Initial studies included prototype electronic boards and mechanical parts to test supply chain capabilities and electronic performance feasibility. The team built on these initial steps by designing the mechanical structure, creating the main electronic control board, sourcing thermal-fluid components, ordering critical pieces, and 3D-printing/laser-cutting parts. Assembly was supplemented with iterative designing, prototyping, and functional testing of individual subsystems. The end of the course brought performance testing to observe alignment with customer requirements, and presenting to relevant project stakeholders. Proper documentation was completed throughout the project, showing clear product development history. By the end, all system and driving customer requirements were met, achieved by persistent, insightful, and collaborative teamwork. However, one derived requirement was not met (CON-05), describing the prohibition of thermal control when the user is handling the PCB. This resulted from a lack of testing with physical PCBs inside the chamber, and implementing the necessary sensors/measurements/controls to enforce this requirement. In spite of this, the team successfully designed, built, and tested the thermally-controlled chamber that met/exceeded most requirements, and served as an enlightening experience for developing well-rounded engineers.
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

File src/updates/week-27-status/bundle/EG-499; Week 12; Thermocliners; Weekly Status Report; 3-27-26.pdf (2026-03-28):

EG-499 Capstone Design

Team Thermocline

Weekly Status Report (Week 12)

Date: 3-27-26

Completed This Week:

- Weekly Meeting (3-26-26; Thursday) – Assembly work and project tasks discussion

Nik (Project Engineer):

- PH

Alex (Chief Test Engineer):

- PH

Lexi (System Engineer):

- PH

Jacob (Chief Analyst):
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

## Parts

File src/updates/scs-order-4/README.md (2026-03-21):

---
date: 2026-03-20
---

# SCS Order 4

For ordering on 3/23

| Setting            | Value          |
|--------------------|----------------|
| Operation          | Sheet Cutting  |
| Material           | 5052 in 0.063" |
| Bends              | Yes            |

Ignore Releif Warnings

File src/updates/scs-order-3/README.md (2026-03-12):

---
date: 2026-03-12
---

# SCS Order 3

For ordering on 3/12

| Setting            | Value          |
|--------------------|----------------|
| Operation          | Sheet Cutting  |
| Material           | 5052 in 0.063" |
| Bends              | Yes            |

Ignore Releif Warnings

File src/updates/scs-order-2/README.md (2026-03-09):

---
date: 2026-03-09
---

# SCS Order 2

For ordering on 3/9

| Setting            | Value          |
|--------------------|----------------|
| Operation          | Sheet Cutting  |
| Material           | 5052 in 0.063" |
| Bends              | Yes            |

Ignore Releif Warnings

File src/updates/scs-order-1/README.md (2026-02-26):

---
date: 2026-02-26
---

# SCS Order 1

For ordering on 2/26

| Setting            | Value          |
|--------------------|----------------|
| Operation          | Sheet Cutting  |
| Material           | 5052 in 0.063" |
| Bends              | Yes            |

Ignore Releif Warnings

2x Side Panels

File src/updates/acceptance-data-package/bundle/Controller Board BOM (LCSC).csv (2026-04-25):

Quantity | LCSC Part # | Description | Designator | Footprint
8 | C1710 | Unpolarized capacitor, small symbol | C201,C203,C301,C303,C401,C403,C601,C603 | C_0805_2012Metric
8 | C49678 | Unpolarized capacitor Unpolarized capacitor, small symbol | C202,C204,C302,C304,C402,C404,C602,C604 | C_0805_2012Metric
4 | C105759 | Unpolarized capacitor | C501,C701,C801,C901 | C_Rect_L13.0mm_W6.0mm_P10.00mm_FKS3_FKP3_MKS4
6 | C258170 | 100V 0.15A standard switching diode, DO-35 | D502,D702,D802,D902,D1002,D1102 | D_DO-35_SOD27_P7.62mm_Horizontal
5 | C142797 | Fuse | F101,F501,F701,F801,F901 | Fuseholder_Littelfuse_100_series_5x20mm
6 | C157931 | Generic connector, single row, 01x02, script generated (kicad-library-utils/schlib/autogen/connector/) | J201,J301,J401,J601,J1001,J1101 | JST_XH_S2B-XH-A_1x02_P2.50mm_Horizontal
1 | C163036 | Generic connector, single row, 01x03, script generated (kicad-library-utils/schlib/autogen/connector/) | J117 | JST_XH_B3B-XH-A_1x03_P2.50mm_Vertical
2 | C263757 | Generic connector, single row, 01x05, script generated (kicad-library-utils/schlib/autogen/connector/) | J114,J116 | JST_XH_S5B-XH-A_1x05_P2.50mm_Horizontal
1 | C163037 | Generic connector, single row, 01x04, script generated (kicad-library-utils/schlib/autogen/connector/) | J113 | JST_XH_S4B-XH-A_1x04_P2.50mm_Horizontal
12 | C532213 | Generic connector, single row, 01x01, script generated (kicad-library-utils/schlib/autogen/connector/) | J101,J102,J103,J104,J105,J106,J107,J108,J109,J110,J111,J112 | Faston 63823
1 | C163036 | Generic connector, single row, 01x03, script generated (kicad-library-utils/schlib/autogen/connector/) | J115 | JST_XH_S3B-XH-A_1x03_P2.50mm_Horizontal
6 | C157931 | Generic connector, single row, 01x02, script generated (kicad-library-utils/schlib/autogen/connector/) | J120,J121,J122,J123,J124,J125 | JST_XH_B2B-XH-A_1x02_P2.50mm_Vertical
4 | C35449 | Sanyo SRD relay, Single Pole Miniature Power Relay, | K501,K701,K801,K901 | Relay_SPDT_SANYOU_SRD_Series_Form_C
1 | C6280121 | 5V, 4A, 20W, Isolated, AC-DC, 219A(IRM20) | PS101 | Converter_ACDC_MeanWell_IRM-20-xx_THT
6 | C124482 | 0.2A Ic, 40V Vce, Small Signal NPN Transistor, TO-92 | Q501,Q701,Q801,Q901,Q1001,Q1101 | TO-92_Inline
2 | C17477 | Resistor, small symbol | R1003,R1103 | R_0805_2012Metric
8 | C17408 | Resistor, small symbol | R202,R203,R302,R303,R402,R403,R602,R603 | R_0805_2012Metric
1 | C2828847 | Resistor, US symbol | R106 | R_0805_2012Metric
8 | C17630 | Resistor, small symbol | R103,R104,R504,R704,R804,R904,R1002,R1102 | R_0805_2012Metric
1 | C114564 | Resistor, small symbol | R105 | R_0805_2012Metric
14 | C95781 C84376 | Resistor, small symbol | R204,R304,R404,R501,R502,R604,R701,R702,R801,R802,R901,R902,R1001,R1101 | R_0805_2012Metric
9 | C84376 | Resistor, small symbol | R101,R102,R107,R108,R109,R503,R703,R803,R903 | R_0805_2012Metric
12 | C17713 | Resistor, small symbol | R1201,R1202,R1204,R1301,R1302,R1304,R1401,R1402,R1404,R1501,R1502,R1504 | R_0805_2012Metric
4 | C107700 | Resistor, small symbol | R201,R301,R401,R601 | R_0805_2012Metric
4 | C722171 | Single Pole Single Throw (SPST) switch | SW501,SW701,SW801,SW901 | SW_TH_Tactile_Omron_B3F-102x
4 | C94571 | Qingxian Zeming Langxi Electronic ZMCT103C current transformer 1000:1 10A | TR1201,TR1301,TR1401,TR1501 | Transformer_Zeming_ZMCT103C
4 | C578736 | Precision Thermocouple Amplifiers with Cold Junction Compensation, K-Type Thermocouple, 0 to 50C, MSOP-8 | U201,U301,U401,U601 | MSOP-8_3x3mm_P0.65mm
1 | C579101 | Single 8-to-1 CMOS Low Voltage 2-Wire Serially Controlled, Matrix Switches | U101 | TSSOP-16_4.4x5mm_P0.65mm
4 | C42463210 | Shunt Regulator, SOT-23 | U202,U302,U402,U602 | SOT-23

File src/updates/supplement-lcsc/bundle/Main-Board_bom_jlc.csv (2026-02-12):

Quantity | LCSC Part # | Description | Designator | Footprint
40 | C142797 | Fuse | F101,F501,F701,F801,F901 | Fuseholder_Littelfuse_100_series_5x20mm
25 | C163037 | Generic connector, single row, 01x04, script generated (kicad-library-utils/schlib/autogen/connector/) | J113 | JST_XH_S4B-XH-A_1x04_P2.50mm_Horizontal
100 | C107700 | Resistor, small symbol | R201,R301,R401,R601 | R_0805_2012Metric
10 | C42463210 | Shunt Regulator, SOT-23 | U202,U302,U402,U602 | SOT-23

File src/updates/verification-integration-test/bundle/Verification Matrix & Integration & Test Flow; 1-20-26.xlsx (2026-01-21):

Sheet: Verification Matrix (VM)
Requirement Type | Performance |  |  |  | Functional |  |  |  | Design |  |  | Interface |  |  |  | Resource |  | Verfication Reference
Requirement Title | Thermal range sweep | Outside Skin Temp | Overall Power Draw | Output Data | Door and Human/Machine | Final Weight | Connectivity | Endurance | Load sizing and Energy | Internal Volume | Safety and Lockouts | HMI (Built in) | HMI (Website) | Door function | Interior Assy. | Thermo-Fluid Safety | Overall Power Draw | This column identifies the specific verfication summary related to the activity on each line. Multiple summaries may apply to a single line item.
Level of Assembly
Structural |  |  |  |  |  |  |  |  |  |  |  |  |  |  |  |  |  | Includes all structural support, fixtures, and attachments of the system.
Frame |  |  |  |  |  | A,T |  | A | A | A,T |  |  |  |  | A,D | D |  | STR-01, STR-02 (frame base dimensions)
Outer Skin |  | T |  |  |  | A,T |  |  |  | D |  |  |  |  |  | D |  | SAF-02 (temperature)
Handles and Contact Points |  |  |  |  |  |  |  | A |  | D |  |  |  |  |  |  |  | STR-03 (insulation), SAF-02 (temperature)
HMI Cover |  | M |  |  | A | T |  |  |  |  |  | A,T |  |  |  |  |  | Includes attachment and protection.
Door | D | A,M |  |  | T | A,T |  | A |  | A,D | A,T |  |  | T |  |  |  | CON-04 (thermal control prohibition)
Electrical Component |  |  |  |  |  |  |  |  |  |  |  |  |  |  |  |  |  | Includes all physical electrical components that support the operation and functionalities.
High Voltage |  |  | A |  |  |  | A,T | A | A,T |  |  |  |  |  |  |  | A,T | System Requirement 2.3 (using standard supplied power)
PCB | D |  | D | A | A |  | T |  |  |  |  | A |  |  |  |  |  | COM-01 (operatable)
HMI interconnect |  |  |  |  | A |  | A,T |  |  |  |  | T | T |  |  |  |  | Interface Requirement 4.1 (HMI control)
Sensors | D | M |  | D |  |  | A |  |  | I | A,T |  |  | D |  |  |  | COM-05 (proper ratings for system operation); includes sufficient room for necessary monitoring/testing components.
Electrical Safety |  |  |  |  |  |  | D | A |  |  | T,D |  |  |  | D |  |  | COM-02, COM-03, COM-04 (proper rules, equipment, specifications)
Lamps and Outputs | D |  |  |  | T |  | A |  |  |  |  |  |  |  |  |  |  | Indicators for operators are tested under all conditions.
Software |  |  |  |  |  |  |  |  |  |  |  |  |  |  |  |  |  | Governs all automatic & manual control of subsystems that support operations.
HMI | D |  |  | T | T |  | A,T |  |  |  |  | T | T |  |  |  |  | Manual device attached to system for external control and monitoring. Some functions can be verified independently from other subsystems.
Website | D |  |  | T |  |  | A |  |  |  |  |  | D |  |  |  |  | Serves for monitoring & ancillary control; verified through testing subsystems.
Controller | D |  | A | T |  |  | A | A,T | D |  |  | D |  | T |  |  |  | CON-1, CON-02, CON-04, CON-05 (control of temperature setpoints and of component when in use)
Thermo-Fluid |  |  |  |  |  |  |  |  |  |  |  |  |  |  |  |  |  | Includes the individual heating and cooling systems and all components that aid in any thermal changes within the chamber.
Assembly (Vacuum Testing) |  |  |  |  |  | A |  |  |  |  |  |  |  |  |  | A |  | Preliminary testing
Layout and Design | T |  |  |  |  |  |  |  |  | A | T |  |  |  | I | T |  | THE-03, THE-04 (containment); no obstruction of different components to structure or functions.
Power Systems | D |  | T |  |  |  | T | A | A,T |  |  |  |  |  |  | T | T | STR-04 (component insulation)
Design Safety |  | M |  |  |  |  |  |  |  |  | T,I |  |  |  |  | T |  | SAF-04, THE-03 (safe-touch from the outside), THE-04 (safe-touch from the outside)
Verification Method: A- Analysis D- Demonstration I- Inspection M- Measurement T- Test V- Validation of Records | Notes: 1. YELLOW: T. BLUE: D. RED: A. GREY: M. 2. Thermo-fluid assembly inlcudes the individual heating and cooling component systems. Assembly testing will need to be proceeded by testing the individual temperature control systems. 3. Each "level of assembly" is a subsystem; the "safety" subsystem is intertwined with the others, and doesn't require it's own level.

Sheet: VM & I&T-F; Notes
Notes:
I&T
1 | Integration and Test (I&T) flow displays the chronology and sequence of activities as a system is assembled and tested
2 | Components are combined into subassemblies, which combine into the assembly or assemblies, and finally the system is ready to be tested.
3 | You can distinguish between "responsibility" (person), "location" (as it pertains to the subassemblies), and "progress" using borders, shapes, or colors in the diagram.
VM
1 | Color-coded to display as much information as possible with as little wording as possible.
2 | Verification Reference section is for tying the data into specific requirements or reports.

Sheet: VM; Example
Requirement Type→ | Performance |  |  | Functional |  |  | Design |  | Interface | Resource |  | Verification Reference
Requirement Title→ | Measure environmental & compost conditions | Connects to system | Meets consistent system power requirements | Indicate threshold reached | Report data to Website | Hold up to 200 kg | Environmentally Friendly | Reliable & Durable | User Friendly | Meets the required budget | Efficient use of materials and resources | This column identifies the specific verification summary related to the activity on each line. Multiple summaries may apply to a single line item.
Level of Assembly
Systems
Arduino (electronics assembly) |  | D | M |  | T |  |  |  | A | V |  | Section 3.3.X Summaries
Sensor Container (housing assembly) |  |  |  |  |  |  | A | A | DI | DM | A | Section 3.3.1 - See Note 2
Door Mechanism |  | D |  |  |  |  | A | T | DI | V | A
Subsystems |  |  |  |  |  |  |  |  |  |  |  | Section 3.2.X Summaries
Electronics Assembly |  | D | M |  | T |  |  |  | A | V |  | Section 3.2.1 - See Note 3
Components |  |  |  |  |  |  |  |  |  |  |  | Section 3.1.X Summaries
MicroController | MV |  |  | T |  |  |  |  | D | V
HMI | MV |  |  | T |  |  |  |  | D | AV
 | M |  |  | VI |  |  |  |  | D | AV
Materials
Refrigerant | M |  |  | VI |  |  |  |  | D | V
Metal Housing | M |  |  | T |  |  |  |  | D | V
 | M |  |  | T |  |  |  |  | D | V
Verification Method: | Notes:
A - Analysis | 1. YELLOW indicates tasks to be done. GREEN indicates completed tasks.
D - Demonstration | 2. Summary References: Resolution (3.3.1), Frame Rate (3.3.2), Mechanical I/F (3.3.3), Electrical I/F (3.3.4), Mass (3.3.5), Power (3.3.6).
I - Inspection | 3. Support electronics used with camera assembly.
M - Measurement
T - Test
V - Validation of Records

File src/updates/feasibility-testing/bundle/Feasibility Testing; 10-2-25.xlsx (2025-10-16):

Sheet: Notes
Date: | Note:
2025-10-02 | Perform at least 3 feasibility tests which touch on aspects of high risk in project. Successful results increase confidence in system. Tests analyze feasibility of performance, resources, project timeline, etc.
2025-10-02 | Contact Jason Crowell for purchasing.
2025-10-07 | Feasibility testing decreases risk of critical components or processes, while improving confidence in system operation, performance, stability, and reliability.

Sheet: Feasibility Test Plan
# | Area of Evaluation | Subsystem | Objective(s) | Test Article | Data to be Collected | Test Support | Instrumentation | Success Criteria
1 | SUPPLY CHAIN CAPABILITY | Electrical/Mechanical | To evaluate (A) effectiveness and (B) efficiency of supply chain by ordering through JLCPCB (electronics) and Send-Cut-Send (small mechanical part/bracket). | Printed Circuit Board ("PCB") prototype & mechanical structural part. | (A) Manufacturer lead time. (B) Price within budget. (C) Company information. (D) Product information. | N/A | Computer --> CAD & ordering part, communicating with supplier. | (A) Component arrives within 2 weeks from initial order. (B) PCB and component match design dimensions. (C) Component arrives with 0 defects hindering operation or performance of PCB. (D) Supplier has good support services.
2 | COMPONENT PERFORMANCE | Mechanical/Thermo-fluid | (A) To verify simultaneous operation of compressor with controller. (B) To confirm performance of compressor meets initial system requirements. | Compressor component. | (A) Component reliability. (B) Operating temperature range. (C) Power consumption. (D) Heat transfer rate. | Table with fixture accodomating compressor and ancillary parts. | Supporting wiring and electrical components for compressor operation. | (A) Compressor functions properly for a continuous 1hr operating period. (B) Effective minimum temperature reaches ≤0oC. (C) Compressor operates successfully when given ≥5 varying thermal setpoints within 1hr.
3 | CONTROL SYSTEM QUALITY | Electrical/Interface | (A) To verify that the HMI screen performs as designed. (B) To verify that the control process from the HMI to an external board, components, and sensors functions as predicted. | Human Machine Interface ("HMI") screen prototype, including touch display and software. | (A) Response time to user input. (B) Touch accuracy and sensitivity. (C) User-friendliness (readability under various lighting conditions). (D) System errors. (E) Power consumption. | (A) Table with fixture accodomating HMI. (B) Lab with sufficient power supply. (C) Controlled lighting environment. (D) Communication cable(s). | (A) Oscilloscope --> measuring signal stability. (B) Data acquisition device / computer --> monitoring & logging HMI data. (C) Camera --> capturing system response. (D) Multimeter --> measuring electrical draw. | (A) No system freezes or input lag (≥500ms over a continuous 1hr operating period). (B) HMI is highly responsive (≤500ms user-input touch to system feedback). (C) Display readability maintained at ≥75% under all test lighting conditions. (D) Power draw within ±10% of HMI design specification.

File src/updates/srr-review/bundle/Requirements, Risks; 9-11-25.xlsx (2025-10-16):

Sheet: System Requirements
Requirement Type | Number | Requirement | Verification Method
Design | 1.1 | The system shall accomodate a 12x12" PCB as device to be tested. | Demonstration
 | 1.2 | The system shall include insulation designed for external safety according to ASTM C1055. | Inspection
 | 1.3 | The system's design shall be safe for continual operation according to NFPA-86. | Inspection
System | 2.1 | The system shall include a port to allow electrical cables to enter and leave for stimulus and measurement of the PCB. | Inspection
 | 2.2 | The system shall comply with electrical grounding requirements. | Inspection
 | 2.3 | The system shall be able to operate on a standard wall-outlet power of 120V (AC). | Demonstration
 | 2.4 | The system will comply with appropriate NEC and UL rules governing powered and plug in devices. | Inspection
Functional | 3.1 | The system shall monitor temperature inside the chamber. | Demonstration
 | 3.2 | The system shall control temperature inside the chamber. | Demonstration
 | 3.3 | The system shall remain within a specified humidity range (0% - 90%). | Demonstration
 | 3.4 | The system shall provide data output. | Demonstration
Interface | 4.1 | The system shall include an HMI for the control system. | Inspection
 | 4.2 | The system shall include separate operating/control modes. | Demonstration

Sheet: Subsystem Requirements
Subsystem | Number | Requirement | Performance | Margin | Verification Method | Basis / Notes | Other Possible Sources:
Mechanical (Structural) | STR-01 | The system shall have external base dimensions of no more than 30x30 inches. | 30x30 in | -2x2 in | Inspection | Analysis | https://store.astm.org/products-services/standards-and-publications/standards/electrical-insulating-material-standards.html
 | STR-02 | The system shall have internal base dimensions of no less than 12x12 inches. | 12x12 in | +2x2 in | Inspection | Analysis
 | STR-03 | The chamber opening(s) shall include proper thermal sealing according to ASTM F1886. | Complies | N/A | Inspection | Maybe: ASTM D5470-17 Test procedure for thermal calculations of seal
 | STR-04 | The internal thermal control components shall include proper thermal sealing according to ASTM C633-01. | Complies | N/A | Inspection | Maybe: ASTM D5470-17 Test procedure for thermal calculations of seal
Mechanical (Thermo-fluid) | THE-01 | The system shall cover commercial temperature range (0oC - 70oC) | 0-70oC | +15oC, -40oC | Measure | Analysis
 | THE-02 | The system shall be capable of sweeping all temperature ranges within a 24-hr cycle. | <24hr | -1hr | Test | Analysis
 | THE-03 | The heating system should be contained/unexposed within the system. | Complies | N/A | Inspection
 | THE-04 | The cooling system should be contained/unexposed within the system. | Complies | N/A | Inspection
Electrical (Component) | COM-01 | The PCB shall be operatable while temperature is controlled. | Complies | N/A | Measure
 | COM-02 | System will adhere to NEC rules on grounding according to Article 250. | Complies | N/A | Inspection | Regulations
 | COM-03 | System will adhere to NEC rules on appropriate fuses and load wire sizes. | Complies | N/A | Inspection | Regulations
 | COM-04 | System will adhere to UL 61010 for test and measurement equipment. | Complies | N/A | Inspection | Regulations
 | COM-05 | The sensors shall be properly rated to withstand internal environmental conditions. | Complies | N/A | Analysis
 | COM-06 | The system shall support PC connection for datalogging. | Complies | N/A | Inspection
Electrical (Control System) | CON-01 | The system shall allow local temperature setpoint control. | Complies | N/A | Test
 | CON-02 | The system shall allow remote temperature setpoint control. | Complies | N/A | Test
 | CON-03 | The system shall maintain a toleranced temperature at ±3oC of setpoint. | ±3oC | ±0oC | Measure | Analysis
 | CON-04 | The system shall prohibit thermal control when the chamber door is open. | Complies | N/A | Demonstration
 | CON-05 | The system shall prohibit thermal control when a user is handling the PCB. | Complies | N/A | Demonstration
 | CON-06 | The system shall log temperature data. | Complies | N/A | Test
 | CON-07 | The system shall log humidity data. | Complies | N/A | Test
 | CON-08 | The system shall log faults for safety measures. | Complies | N/A | Measure
 | CON-09 | The system shall have a "shutdown" state. | Complies | N/A | Demonstration
 | CON-10 | The system shall have a "standby" mode. | Complies | N/A | Demonstration
 | CON-11 | The system shall have a normal operating "start" mode. | Complies | N/A | Demonstration
 | CON-12 | The system shall allow for manual switching between modes. | Complies | N/A | Demonstration
Safety | SAF-01 | The internal surfaces shall be safe for electronics according to ASTM D3874-20. | Complies | N/A | Analysis
 | SAF-02 | The system external surfaces shall not exceed the safe-touch temperature of 50oC according to ASTM C1055. | 50oC | -7oC | Analysis | Analysis
 | SAF-03 | The system shall be able to operate in normal environmental (external) conditions of 21oC. | 21oC | ±5oC | Demonstration | Analysis
 | SAF-04 | The system shall include a safety measure if temperature range & tolerance is exceeded. | Complies | N/A | Demonstration
 | SAF-05 | The system shall have a "safe" state. | Complies | N/A | Demonstration

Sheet: Other Tables
Requirement Types | Examples
Design | Structural, Stiffness, Materials, Reliability, Redundancy, Electronic Parts
Environmental | Temperature, RH, Pressure, Vibration, EMC/EMI, Cleanliness
Functional | Operating Modes, Software, Mechanism Control, Autonomous Mode
Interface | Power Supply, Data Handling, Mounting, Thermal
Performance | Resolution, Focus, Sampling Rate, Jitter Control
Project | Program Management, Systems Engineering, Quality Assurance
Resource | Mass, Weight, Physical Size, Power, Data Volume, Data Rate, Field-of-View
Safety | Personal Protective Equipment, Machine Guards
Verification | Models, Methods, Levels
Verification Method | Description
Analysis | By mathematically modeling or simulating the system, it is predicted that a requirement is met or not.
Demonstration | By doing something with the system, it is clear if the requirement is met or not.
Inspection | By observing the system, it is clear if the requirement is met or not.
Measure | By collecting multiple measurements, it is clear if the requirement is met or not.
Test | By collecting a single measurement, it is clear if the requirement is met or not.
Subsystem | Classification
Mechanical (structural) | STR
Mechanical (thermo-fluid) | THE
Electrical (component) | COM
Electrical (control system) | CON
Safety | SAF
Basis | Description
Analysis
Research
Regulations
Customer

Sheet: Project Risks
Risk Matrix |  |  |  |  |  |  |  |  |  | Consequence Category | PRE-MITIGATION |  |  |  |  |  |  | POST-MITIGATION
Consequence | 5 | B, L | A, E, P | K, M, O | Z |  | Letter | Consequence | Description | Asset
 | 4 |  | Y | N | I | Q, W | A | Asset | Mechanical Failure of Components (worn, broken) | Cost | Consequence | 5 |  |  |  | Z |  | Consequence | 5
 | 3 |  | F, G | T, U, X | V |  | B | Asset | Insufficient Dimensions for PCB testing (internal, external, cable port, chamber door) | Human Safety |  | 4 |  |  |  |  | Q, W |  | 4 |  | Z
 | 2 | R | J |  | C, D | H | C | Asset, Human Safety | Internal System is Over Temperature Range (fire, melting components) | Performance |  | 3 |  |  |  |  |  |  | 3 |  |  |  | Q
 | 1 | S |  |  |  |  | D | Asset, Human Safety | Internal System is Under Temperature Range (freezed components) | Schedule |  | 2 |  |  |  |  |  |  | 2 |  |  |  | W
 |  | 1 | 2 | 3 | 4 | 5 | E | Asset, Performance | System's Safety Measure Fails If Outside Temperature Range |  |  | 1 |  |  |  |  |  |  | 1
 |  | Likelihood |  |  |  |  | F | Asset, Performance | Internal Heating/Cooling System Can't Reach upper/lower boundaries (poor components, inefficient controller) |  |  |  | 1 | 2 | 3 | 4 | 5 |  |  | 1 | 2 | 3 | 4 | 5
Notes: | Combined Risk Scores: 0-9 (Green) --> Minor 10-19 (Yellow) --> Moderate 20-29 (Red) --> Major |  |  |  |  |  | G | Asset, Performance | Inconsistent Temperature Control (poorly designed microcontroller or interface) |  |  |  | Likelihood |  |  |  |  |  |  | Likelihood
 |  |  |  |  |  |  | H | Asset, Performance | Failure to Maintain Toleranced Setpoint (±o3C) (ineffective control system, poor insulation - internal & external) |  | Notes: | Combined Risk Scores: 0-9 (Green) --> Minor 10-19 (Yellow) --> Moderate 20-29 (Red) --> Major |  |  |  |  |  | Notes: | Combined Risk Scores: 0-9 (Green) --> Minor 10-19 (Yellow) --> Moderate 20-29 (Red) --> Major
 |  |  |  |  |  |  | I | Asset, Performance | Lack of Electronic Protection (excessive moisture buildup)
 |  |  |  |  |  |  | J | Cost | Spending Past Designated Budget for Equipment & Materials
 |  |  |  |  |  |  | K | Human Safety | Lack of Human Protection at Critical Temperature Ranges (burns)
 |  |  |  |  |  |  | L | Human Safety | System Fails to Meet Environmental/Engineering Codes
 |  |  |  |  |  |  | M | Human Safety | System Fails to Prohibit Temperature Control During Manual User Usage.
 |  |  |  |  |  |  | N | Human Safety, Performance | Chemical Leaking
 |  |  |  |  |  |  | O | Human Safety, Performance | Electrical Hazards (short circuits, improper connections)
 |  |  |  |  |  |  | P | Human Safety, Performance | System Fails to Operate Safely Under Normal Conditions
 |  |  |  |  |  |  | Q | Performance | Software/HMI Failure
 |  |  |  |  |  |  | R | Performance | Lack of Refrigerant Fluid in System
 |  |  |  |  |  |  | S | Performance | Controller not User Friendly (poor HMI design)
 |  |  |  |  |  |  | T | Performance | Sensor Reading Failure (miscalibration, component issue)
 |  |  |  |  |  |  | U | Performance | Improper Ventilation (pressure changes, fumes buildup)
 |  |  |  |  |  |  | V | Performance | Ineffective Insulation (poor materials or design)
 |  |  |  |  |  |  | W | Performance | Data Measuring, Collecting, and Logging Fail to Work Systematically
 |  |  |  |  |  |  | X | Performance | System Mode(s) Failures
 |  |  |  |  |  |  | Y | Schedule | Poor Scheduling for Fabricated Parts or Sourced Materials
 |  |  |  |  |  |  | Z | Schedule, Cost | Rework of Product (ineffective design from failed systems/components/materials)

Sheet: Verification Matrix (Example)
Requirement Type→ | Performance |  |  | Functional |  |  | Design |  | Interface | Resource |  | Verification Reference
Requirement Title→ | Measure environmental & compost conditions | Connects to system | Meets consistent system power requirements | Indicate threshold reached | Report data to Website | Hold up to 200 kg | Environmentally Friendly | Reliable & Durable | User Friendly | Meets the required budget | Efficient use of materials and resources | This column identifies the specific verification summary related to the activity on each line. Multiple summaries may apply to a single line item.
Level of Assembly
Systems
Arduino (electronics assembly) |  | D | M |  | T |  |  |  | A | V
Sensor Container (housing assembly) |  |  |  |  |  |  | A | A | A | V | A
Door Mechanism |  | D |  |  |  |  | A | T | T | V | A
Components
MicroController | M |  |  | T |  |  |  |  | D | V
HMI | M |  |  | T |  |  |  |  | D | V
 | M |  |  | T |  |  |  |  | D | V
Materials
Refrigerant | M |  |  | T |  |  |  |  | D | V
Metal Housing | M |  |  | T |  |  |  |  | D | V
 | M |  |  | T |  |  |  |  | D | V
Verification Method: | Notes:
A - Analysis | 1. YELLOW indicates tasks to be done. GREEN indicates completed tasks.
D - Demonstration
I - Inspection
M - Measurement
T - Test

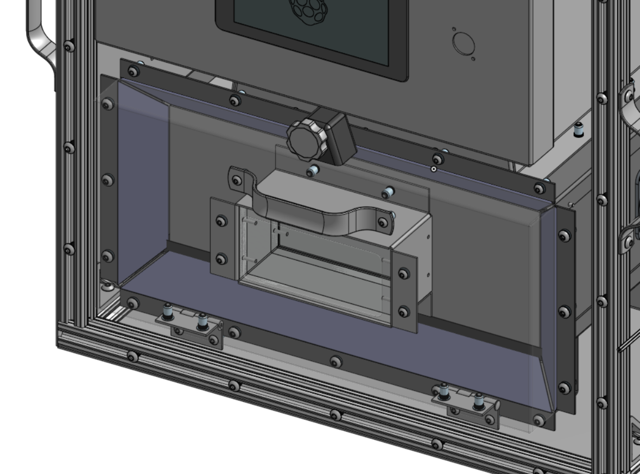
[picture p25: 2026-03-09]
src/updates/scs-order-2/preview.png

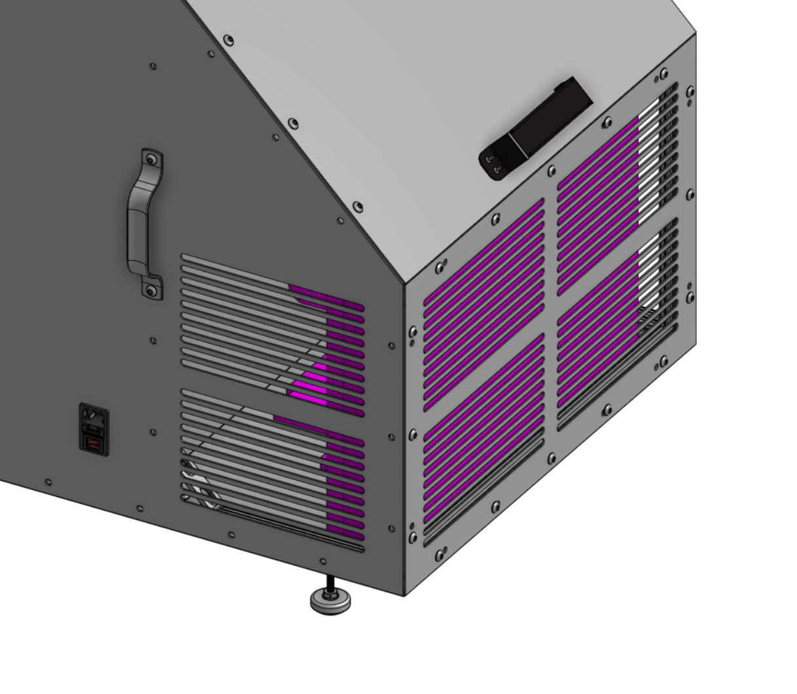
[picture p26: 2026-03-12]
src/updates/scs-order-3/preview.png

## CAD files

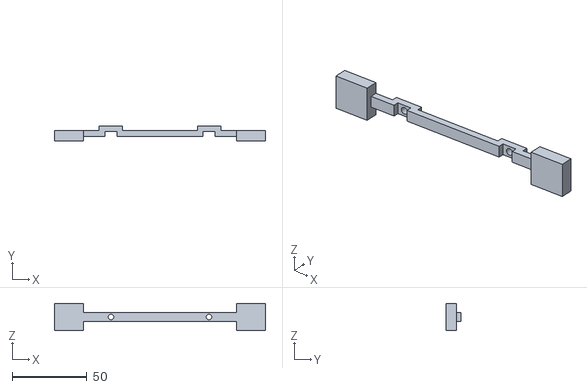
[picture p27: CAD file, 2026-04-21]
src/updates/3d-printing-kit/bundle/Screen backing2.1.stl
141.3 x 10.0 x 18.3

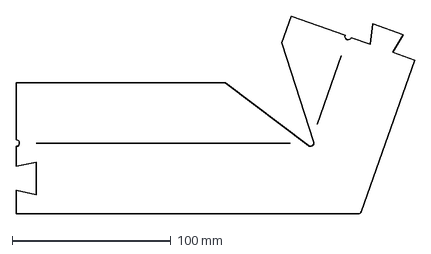
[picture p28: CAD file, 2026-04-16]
src/updates/gasket-kit/bundle/Gaskets/Primary Door Gasket A.dxf
250.8 x 124.2 mm

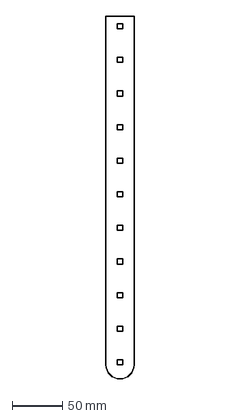
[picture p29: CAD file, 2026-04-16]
src/updates/gasket-kit/bundle/Tape/LED Tape.dxf
27.9 x 361.9 mm

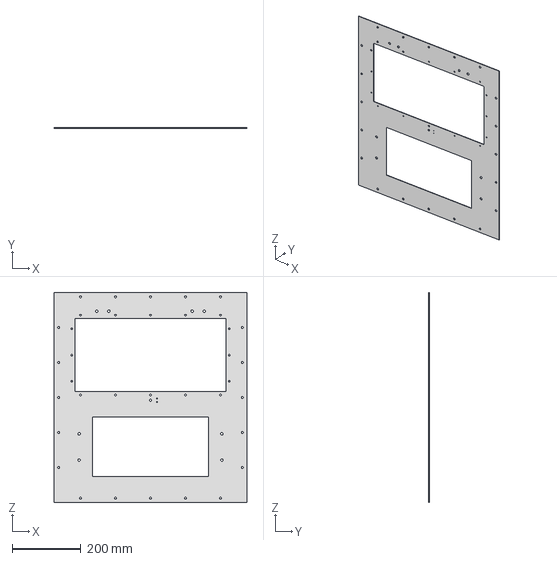
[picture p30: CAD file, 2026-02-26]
src/updates/scs-order-1/bundle/Front Panel; 3.stp
558.8 x 1.60 x 609.6 mm

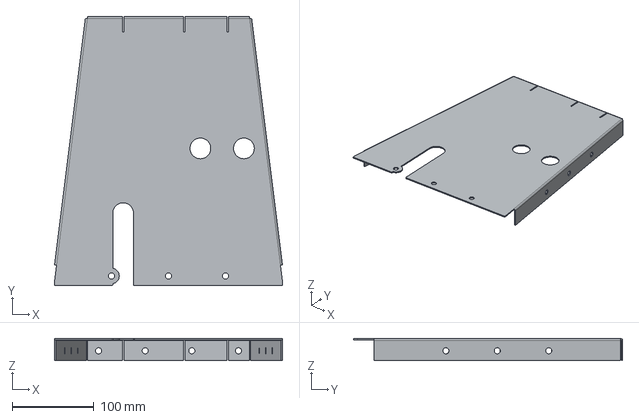
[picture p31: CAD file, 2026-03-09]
src/updates/scs-order-2/bundle/Air Transfer Compartment; Back Panel 7.stp
279.4 x 330.2 x 27.0 mm

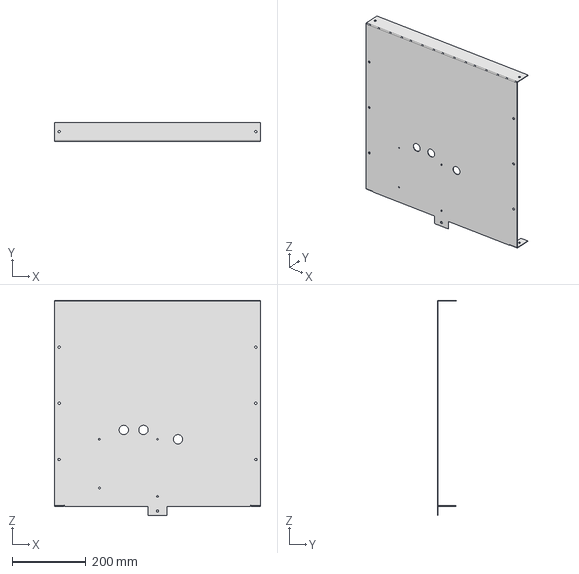
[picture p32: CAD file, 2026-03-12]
src/updates/scs-order-3/bundle/Partition Panel; 4.stp
558.8 x 52.4 x 584.2 mm

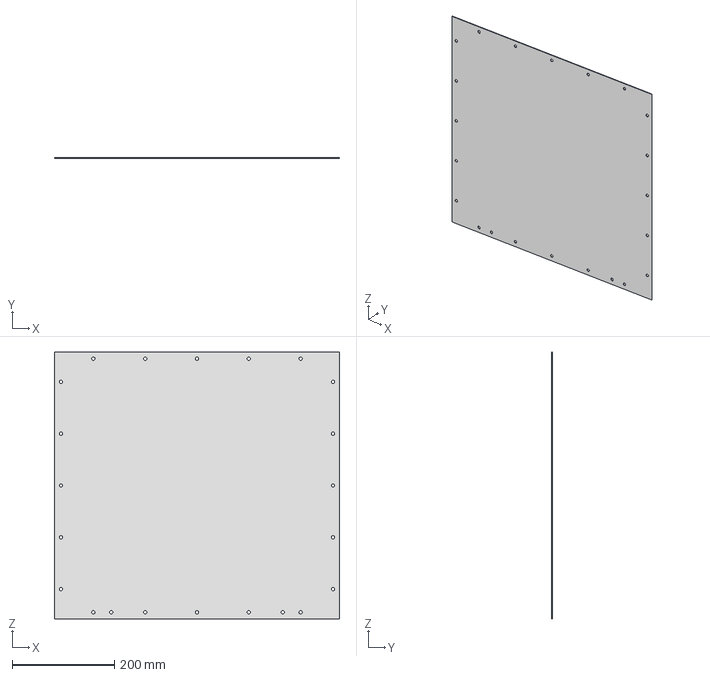
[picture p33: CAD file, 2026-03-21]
src/updates/scs-order-4/bundle/Top Panel; A; 2.stp
558.8 x 1.60 x 522.6 mm

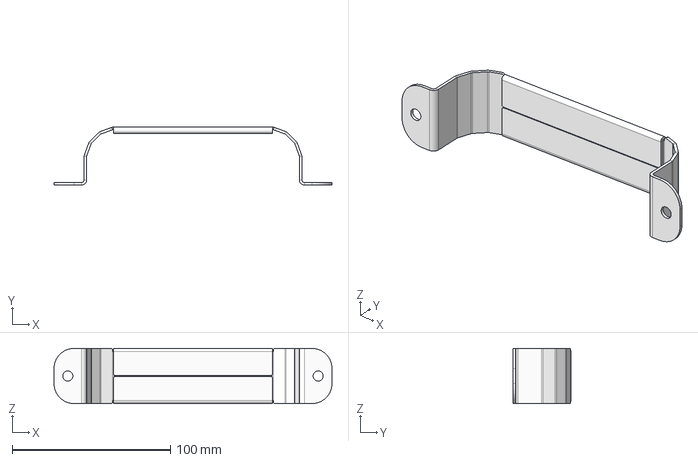
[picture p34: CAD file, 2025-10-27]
src/updates/sheet-metal/bundle/Chamber; External Door Handle; 10-22-25.stp
175.7 x 36.6 x 34.9 mm

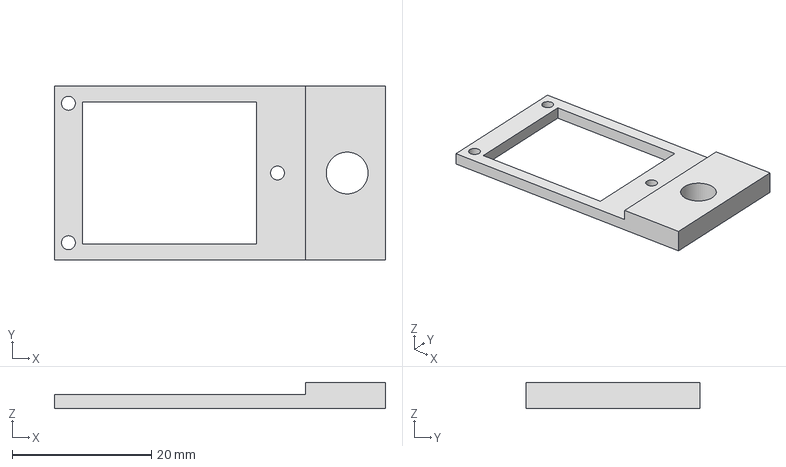
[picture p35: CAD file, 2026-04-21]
src/updates/3d-printing-kit/bundle/Humidity holder.stp
47.5 x 25.0 x 3.78 mm

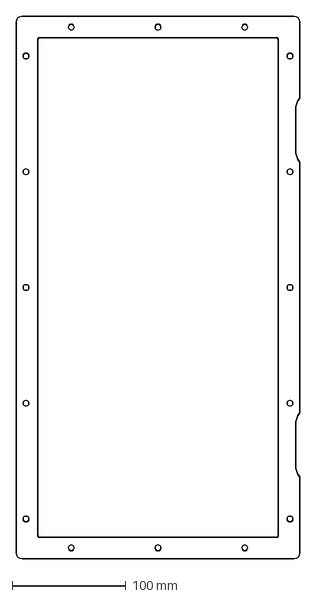
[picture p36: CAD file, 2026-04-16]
src/updates/gasket-kit/bundle/Gaskets/Front Gasket.dxf
248.8 x 476.5 mm

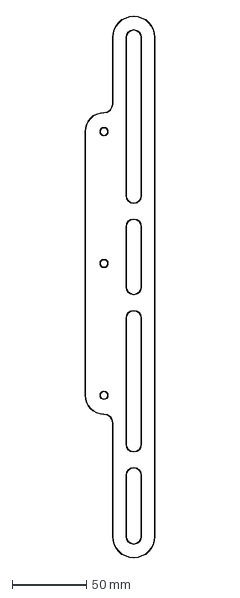
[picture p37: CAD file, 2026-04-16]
src/updates/gasket-kit/bundle/Tape/LED Support.dxf
47.0 x 365.0 mm

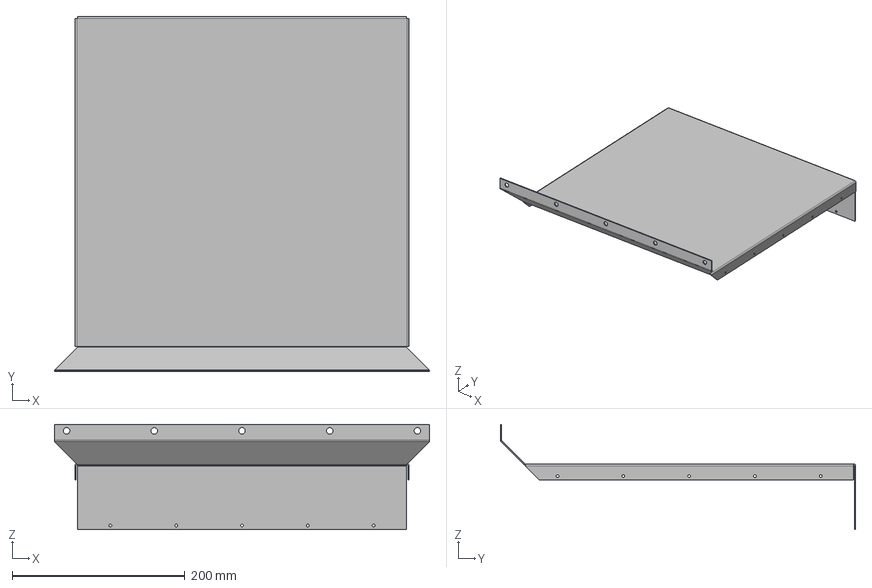
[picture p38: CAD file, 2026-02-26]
src/updates/scs-order-1/bundle/Internal Top (Bottom) - Inner tops.step
434.4 x 411.8 x 121.8 mm

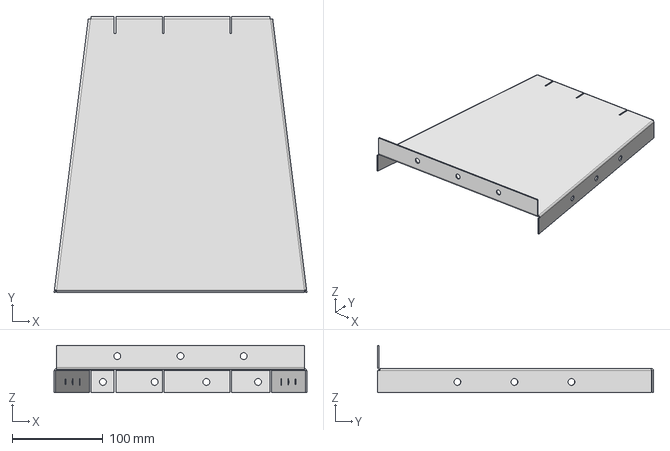
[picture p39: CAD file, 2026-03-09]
src/updates/scs-order-2/bundle/Air_Transfer_Compartment__Front_Panel__5.stp
279.4 x 305.0 x 52.4 mm

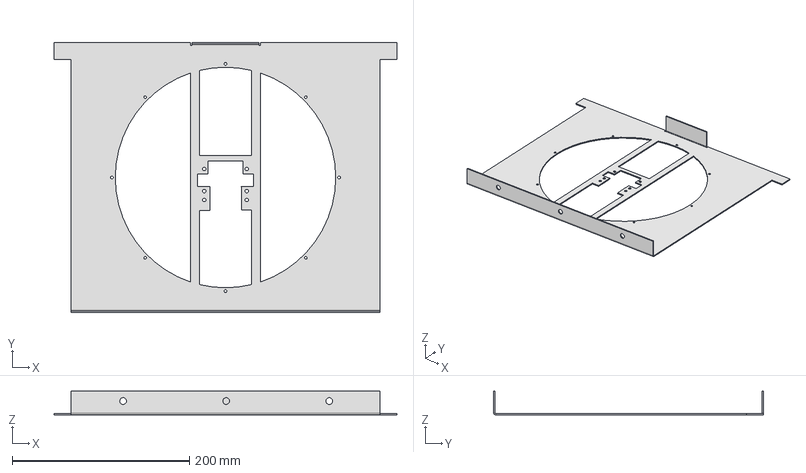
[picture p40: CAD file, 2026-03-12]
src/updates/scs-order-3/bundle/Fan holder.stp
387.3 x 304.8 x 27.0 mm

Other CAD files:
src/updates/scs-order-4/bundle/Top Panel; B; 4.stp
src/updates/sheet-metal/bundle/Tweaks-Repalcement Body.step
src/updates/3d-printing-kit/bundle/Under Fan.stp
src/updates/gasket-kit/bundle/Gaskets/Bezel Gasket.dxf
src/updates/3d-printing-kit/bundle/Cap Carrier-Back.stl
src/updates/3d-printing-kit/bundle/Cap Carrier-Front.stl
src/updates/3d-printing-kit/bundle/Condensation Side Plug A; v1.stl
src/updates/3d-printing-kit/bundle/Door Sensor Covering; v2.stl
src/updates/3d-printing-kit/bundle/Door Sensor Mount; 2.stl
src/updates/3d-printing-kit/bundle/Evap Carrier-Back.stl
src/updates/3d-printing-kit/bundle/Evap Carrier-Front.stl
src/updates/3d-printing-kit/bundle/Fan Duct.stl
src/updates/3d-printing-kit/bundle/Partition Wall Plug A; v1.stl
src/updates/3d-printing-kit/bundle/Plugs and Misc-Power Plug.stl
src/updates/3d-printing-kit/bundle/Power Plug Cover; v2.stl
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

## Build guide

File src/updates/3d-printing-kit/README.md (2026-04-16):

---
date: 2026-04-16
---

# 3D Printing Kit

All 3D printed parts at your convenience! 

If any printed parts break, look here first!

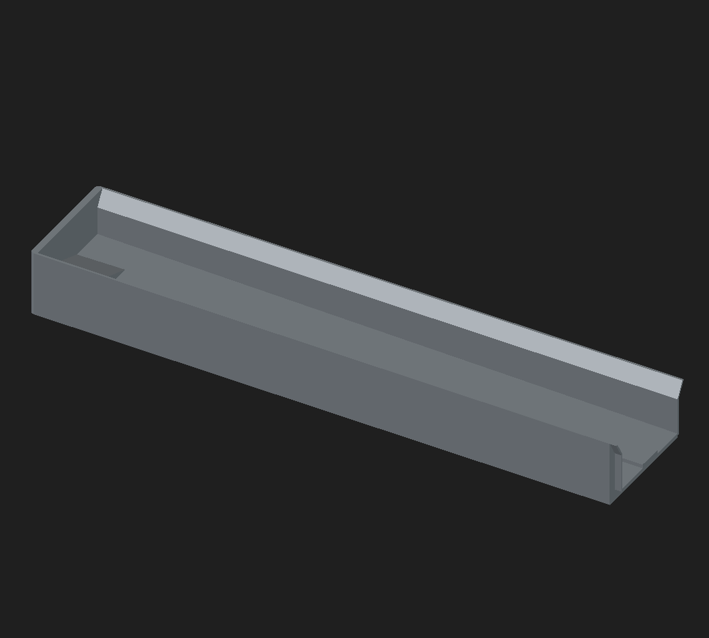
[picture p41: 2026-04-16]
src/updates/3d-printing-kit/preview.png

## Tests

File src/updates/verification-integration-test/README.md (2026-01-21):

---
date: 2026-01-21
---

# Verification Matrix, Integration & Testing

Thanks whole team for working so hard on this. Submitted wednesday morning.

Bundle includes matrix, references and I&T Flow!

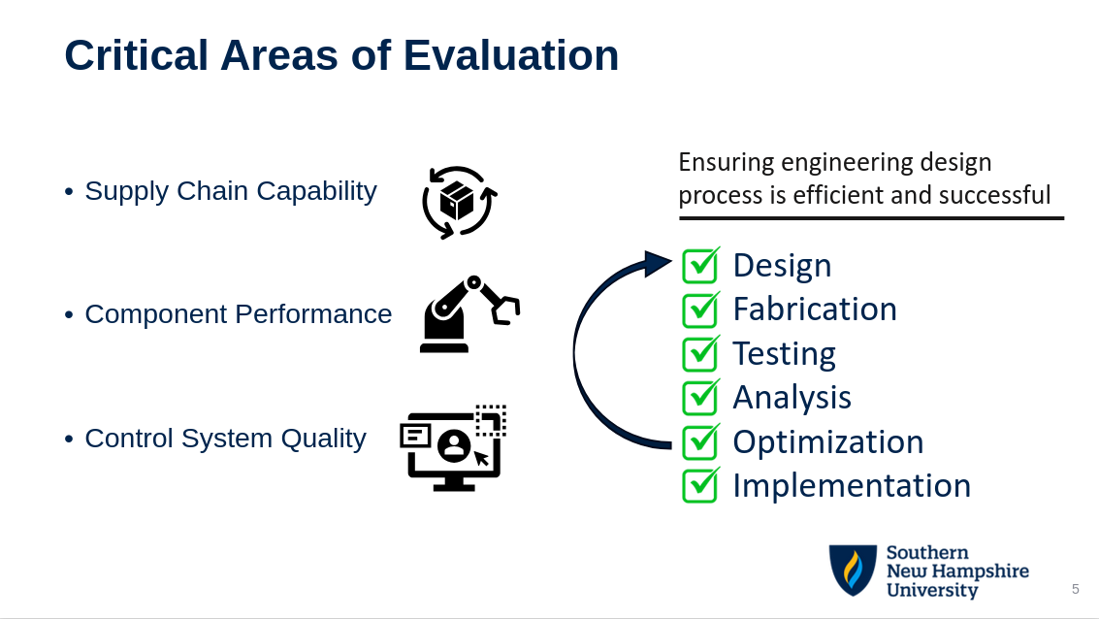
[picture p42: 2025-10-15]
src/updates/feasibility-testing/preview.png

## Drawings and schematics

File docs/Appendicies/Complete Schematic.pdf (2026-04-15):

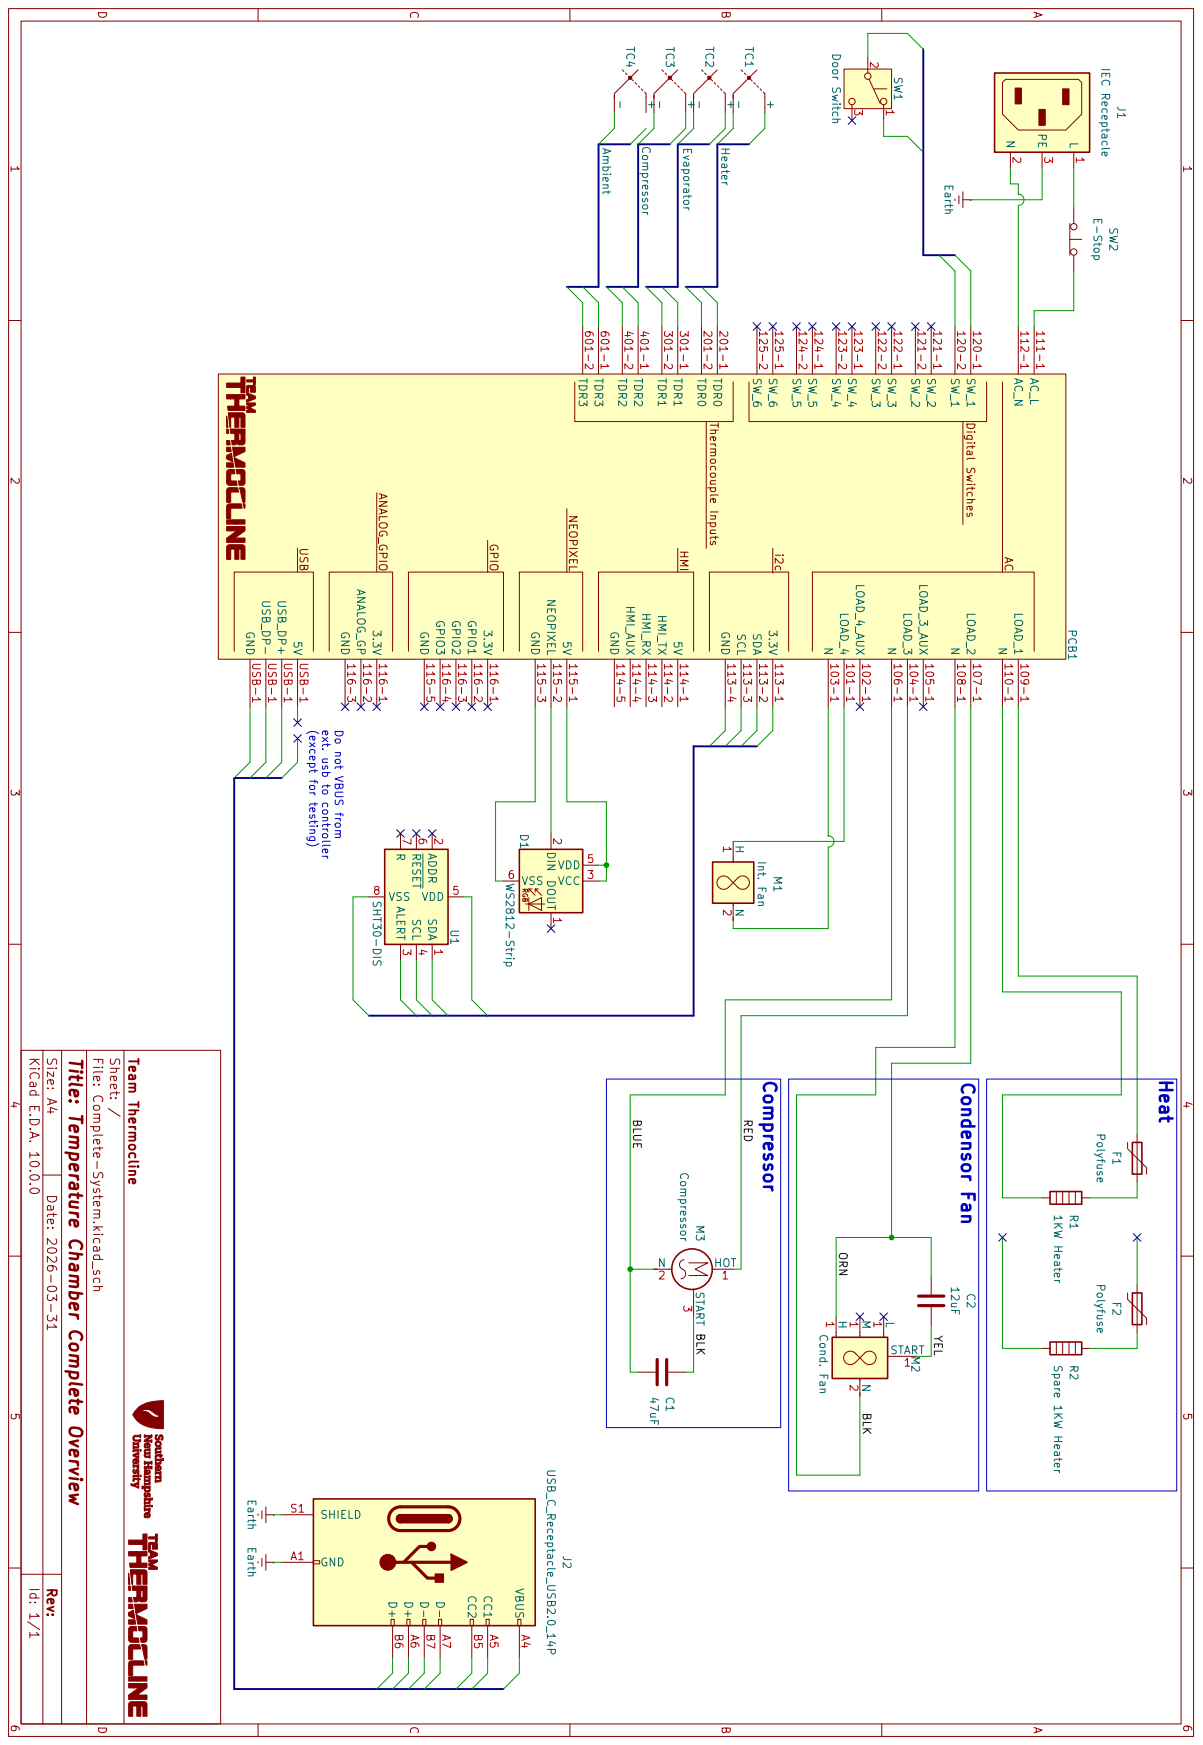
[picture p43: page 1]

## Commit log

2025-10-16 Replace bundle.zips with bundle/ dirs
    [Feasibility Testing; 10-2-25.xlsx, Requirements, Risks; 9-11-25.xlsx]
2025-10-21 Adapter board submitted!
2025-10-27 Publish sheet metal
    [Chamber; External Door Handle; 10-22-25.stp, Chamber; External Door Handle; 2; 10-23-25.ipt, Tweaks-Repalcement Body.step, Tweaks.FCStd]
2025-10-29 Boards have arrived! And new tool~
2026-01-16 Add PCB layout viewer (temporary-ish)
2026-01-19 Change url for pcb:
2026-01-21 Add V I&T and RSS
    [Verification Matrix & Integration & Test Flow; 1-20-26.xlsx]
2026-01-29 Update sch and pcb to v1.0 build
2026-02-02 Sender 2.0 (#1)
    Still has some things to add but this is good enough for a prototype!
2026-02-08 Boards update
2026-02-09 Enable door sensor
2026-02-12 Make new LCSC order, add new timeline target
    [Main-Board_bom_jlc.csv]
2026-02-26 Thank you Jacob for the CAD work! This order is ready to go
    [Front Panel; 3.stp, Internal Top (Bottom) - Inner tops.step, PCB Compartment Stand; 2.stp, PCB Compartment; Side; A; 1.stp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]
2026-03-09 Add SCS #2
    [Air_Transfer_Compartment__Back_Panel__6.stp, Air_Transfer_Compartment__Front_Panel__5.stp, Air_Transfer_Compartment__Top_Panel__Split_A__1__Trial_1.stp, Front_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]
2026-03-09 Fix slot on panel 7 (Air transfer compartment back)
    [Air Transfer Compartment; Back Panel 7.stp, Air_Transfer_Compartment__Back_Panel__6.stp]
2026-03-09 Okay, i couldn't leave it alone, sorry jacob!
    [Air Transfer Compartment; Back Panel 7.stp]
2026-03-12 SCS Order 3
    [Fan holder.stp, Front Door Back Panel; 5.stp, Partition Panel; 4.stp, Rear Panel; 4.stp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]
2026-03-17 Add power metric
2026-03-21 Add scs order 4
    [Bottom Panel; 0.187; 2.stp, Chamber Strap; 1.stp, Top Panel; A; 2.stp, Top Panel; B; 4.stp]
2026-04-11 Allow for graphing/export of ALL temp sensors
2026-04-16 Gasket kit
    [Bezel Gasket.dxf, Front Gasket.dxf, LED Support.dxf, LED Tape.dxf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]
2026-04-16 Add 3d printed parts kit
    [Cap Carrier-Back.stl, Cap Carrier-Front.stl, Condensation Side Plug A; v1.stl, Door Sensor Covering; v2.stl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]
2026-04-20 Add poweron missing image
2026-04-21 Add Alex and Lexi's parts
    [Humidity holder.stp, Screen backing2.1.stl, Under Fan.stp, evaporator top.stp]
2026-04-25 Final report and ADP
    [Controller Board BOM (LCSC).csv]
